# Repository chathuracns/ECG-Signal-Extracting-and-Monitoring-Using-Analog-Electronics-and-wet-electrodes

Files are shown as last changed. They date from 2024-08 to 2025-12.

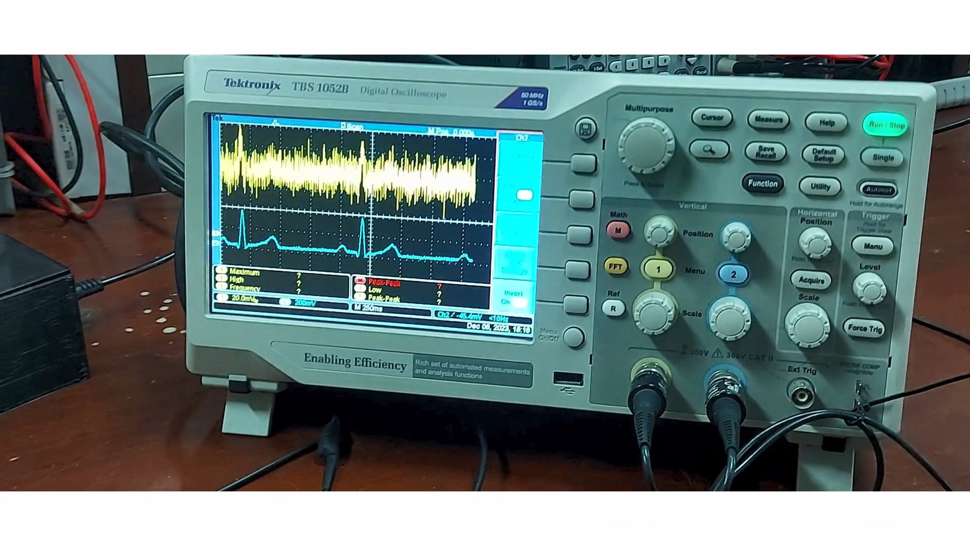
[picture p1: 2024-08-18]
media/amplified signal and denoised signal.png

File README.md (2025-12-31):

# Analog Heart Rate Monitor

## Overview
This project is an ECG (Electrocardiogram) waveform output and display heart monitor developed by a team of students from the Department of Electronic & Telecommunication Engineering, University of Moratuwa, Sri Lanka. The device is designed to amplify and display the small ECG voltage signal (0.1 mV to 10mV) while effectively managing noise interference.
[Video](https://www.linkedin.com/posts/chathura-weerasinghe-9a08bb213_ecg-biomedicalengineering-analogelectronics-activity-7230936167209189376-2sdM?utm_source=share&utm_medium=member_desktop)
## Features
- Right Leg Drive circuit for common-mode signal cancellation
- Instrumentation Amplifier for signal amplification and common noise elimination
- 1st order active Butterworth high pass filter
- 5th order active Bessel Thompson low pass filter
- Twin-T style notch filter for power line interference removal
- Analog components used throughout (except for the display unit)
- Adjustable gains and cutoff frequencies via variable resistors
- Custom-designed PCB and 3D-printed enclosure

## System Architecture
The system consists of the following main components:
1. Right Leg Drive Circuit
2. Instrumentation Amplifier
3. High Pass Filter
4. Low Pass Filter
5. Notch Filter
6. Power Supply Circuit
7. Display Circuit

## Key Components
- Operational Amplifier: TL072CP

## PCB Design
- Designed using Altium Designer
- Three separate PCBs: power circuit, heart monitor circuit, and display circuit
- Multi-layer design with ground pour and power routing

## Enclosure
- Designed using Solidworks
- Features removable top cover and detachable front for easy maintenance
- Includes power switch, tuning knob, and strategically placed connectorsi

## Contributors
- Kumarasinghe R.D (210321X)
- Rajapakshe N.N (210504L)
- Weerasinghe C.N (210687X)
- Withanawasam I.A (210732H)

## Acknowledgements
This project was submitted in partial fulfillment of the requirements for the module EN 2091 Laboratory Practice and Projects at the University of Moratuwa, Sri Lanka.

## License
GNU GENERAL PUBLIC LICENSE

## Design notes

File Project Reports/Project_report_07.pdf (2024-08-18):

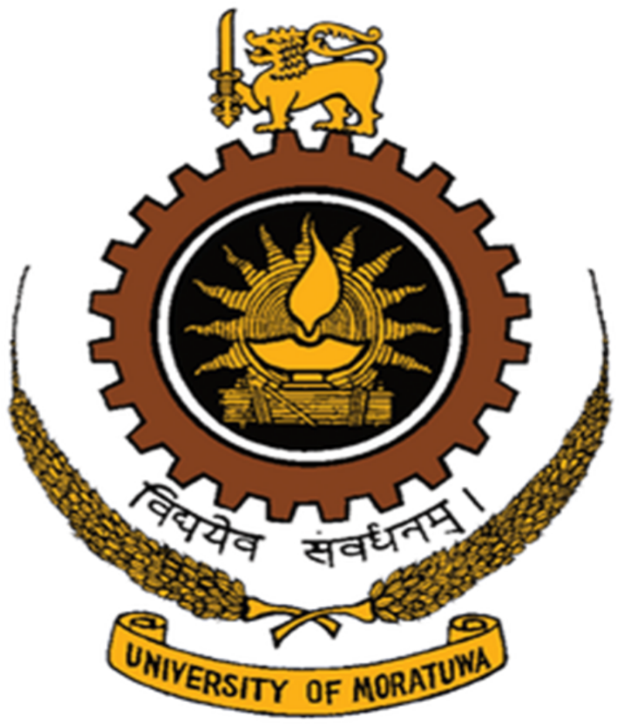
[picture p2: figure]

Department of Electronic & Telecommunication Engineering, University of Moratuwa, Sri Lanka.

# Analog Heart Rate Monitor

Group Members:

210321X | Kumarasinghe R.D
210504L | Rajapakshe N.N
210687X | Weerasinghe C.N
210732H | Withanawasam I.A

Submitted in partial fulfillment of the requirements for the module EN 2091 Laboratory Practice and Projects

6th December 2023

Analog Heart Rate Monitor | Group 07

## Contents

1 Introduction | 2
2 Functionality and Parameters | 2
2.1 Right Leg Drive | | | 2
2.2 Instrumentation Amplifier | | | 3
2.2.1 | Gain of the Instrumentation Amplifier | | 3
2.3 High Pass Filter | | 3
2.3.1 | Gain and Cutoff Frequency of High Pass Filter | | 3
2.4 Low Pass Filter | | 3
2.4.1 | Cutoff Frequency of Low Pass Filter | | 3
2.5 Notch Filter | | 3
2.5.1 | Cutoff Frequency of Notch Filter | | 4
3 System Architecture | 4
4 Component Selection | 4
5 PCB Design | 5
6 Enclosure Design | 5
7 Software Simulation and Hardware Testing | 5
8 Conclusion & Future Works | 5
9 Contribution of Group Members | 6
10 Bill of Materials | 6
11 References | 6
12 Appendix | 7

1

Abstract
Our project is an ECG waveform output and display heart monitor.The difficult task is to make the small range of the ECG voltage signal: 0.1 mV to 10mV, which is significantly impacted by noise.This is accomplished by a leg drive circuit, an a high pass filter, an instrumentation amplifier,both a notch filter and a low pass filter were utilized. 160 Hz was the bandwidth that was taken into consideration. Attaining this requires only analog electronic parts were employed. electronic digital elements were exclusively utilized in the digital circuit, breadboard, and simulation testing testing was carried out, along with PCB testing. the circuit’s functionality. An 3D enclosure was created and constructed to meet the requirements.

## 1 Introduction

An electrocardiogram (ECG) is a quick test that uses skin-attached sensors to measure electrical signals the heart produces with each beat in order to assess the heart’s rhythm and electrical activity. There is an increase in voltage between the right and left arms, with the right leg acting as a feedback mechanism. The ECG leads are used to obtain the voltages of the right arm, left arm, and right leg . The voltage signal’s frequency ranges from 0.01 Hz to 250 Hz, while its amplitude spans 0.1 mV to 10 mV.The small amplitude of the ECG raw signals and their susceptibility to noise and disturbances like electrostatic potentials, power line interference, RFI, electrode contact noise, stray capacitance, and bio signal artifacts introduced into an ECG by subject movement, respiration, and muscle tension make it difficult to amplify this signal. The ECG waves may occasionally be overpowered by noise, rendering the amplified signal meaningless.
We used only analog components when designing the ECG monitor, with the exception of the display unit, which amplifies and shows the voltage waveform mentioned above. We have described how we accomplished this in this report. The circuits listed below were used to generate the ECG waveform and provide the desired result.
1. Right Leg Drive Cicruit
2. Instrumentation Amplifier
3. 1st order active Butterworth high pass filter
4. 5th order active Bessel Thompson low pass filter
5. The Notch Filter

Moreover, the power supply and display screen were each connected to a different circuit, each with its own PCB. Variable resistors have been used in each filter circuit to modify the gains, reduce noise and disturbances based on the location, and compensate for unstable power supplies.

## 2 Functionality and Parameters

### 2.1 Right Leg Drive

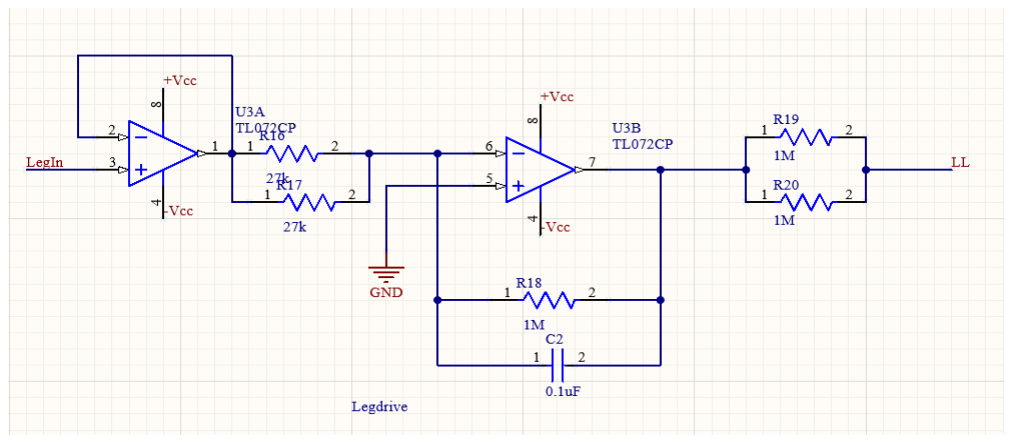
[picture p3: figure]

Figure 1: Right Leg Drive Circuit

By inverting, amplifying, and then feeding the signal back to the body through the right leg electrode, a right leg drive circuit is used to cancel the common-mode signal between the left and right arm electrodes.Additionally, the high value resistors in this circuit make sure that the patient is not exposed to a higher current.

2

### 2.2 Instrumentation Amplifier

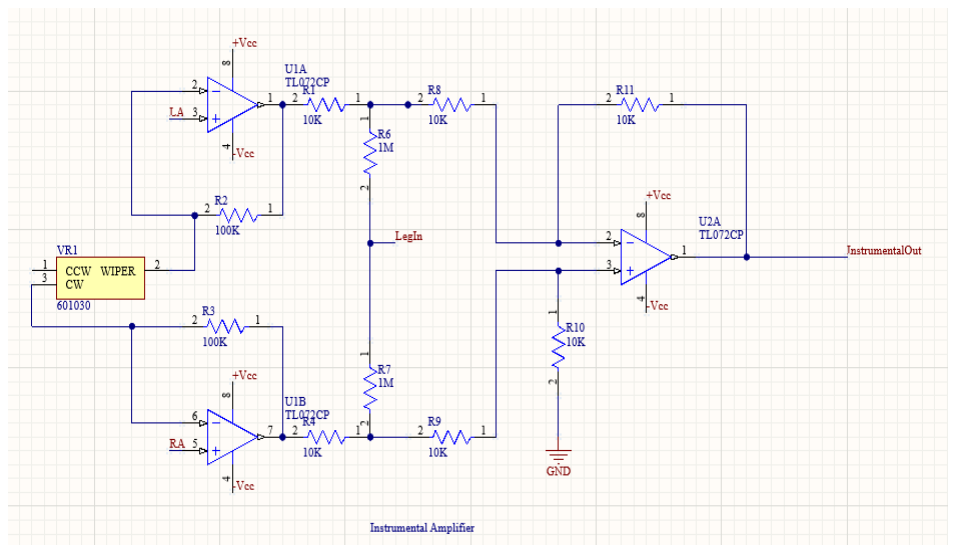
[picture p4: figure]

Figure 2:Instrumentation Amplifier

The signal is amplified using this circuit, which also eliminates common noise from the voltages coming from the ECG leads. This circuit converts the three inputs into a single output. Our circuit’s gain in the instrumentation amplifier is maintained between 20 and 50. We have adjusted the gain as needed by using a variable resistor.

### 2.2.1 Gain of the Instrumentation Ampli-

fier

Gain = R10
R9

(

R2 + R3 + V R1
V R1

)

Minimum Gain = 10kΩ
10kΩ(

2 × 100kΩ + 10kΩ
10kΩ | )
Minimum Gain = 21

### 2.3 High Pass Filter

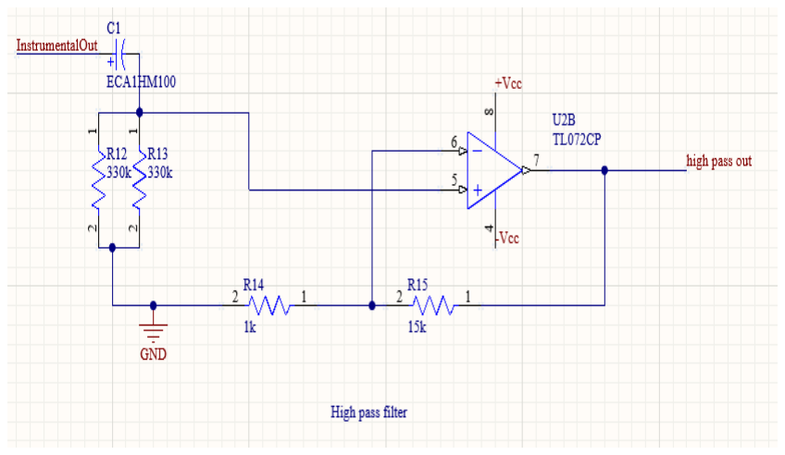
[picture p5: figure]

Figure 3:High Pass Filter

A first-order active inverting Butterworth filter has been used. In addition to amplifying the signal even more, this circuit removes the DC offset that developed between the electrodes. The gain of the filter is 16.

### 2.3.1 Gain and Cutoff Frequency of High

Pass Filter

Cutoff Frequency(Fc) = | 1 2π(R12//R13)C1
Cutoff Frequency = | 1 2π × 165kΩ × 10µF

Fc = 0.0965Hz

Gain =1 + R15

R14
Gain = 1 + 15kΩ
1kΩ = 16

### 2.4 Low Pass Filter

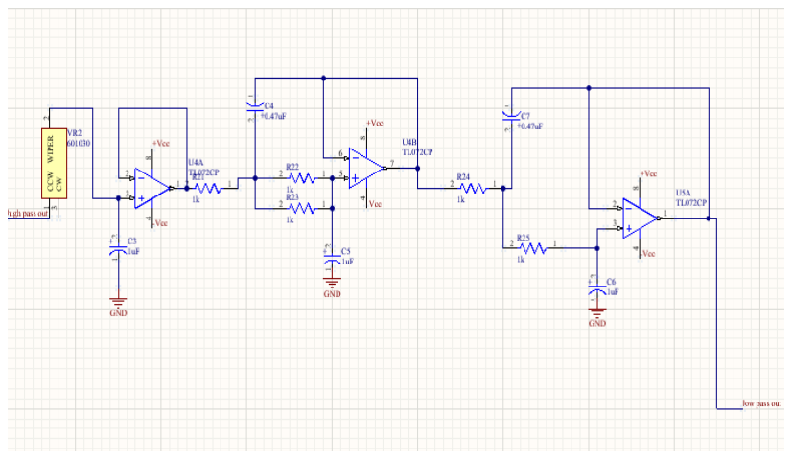
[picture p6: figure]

Figure 4:Low Pass Filter

Here, we employed a non-inverting Bessel Thompson filter of the fifth order. Two second order active filters and a series cascaded first order active filter make up this setup. Since each of their gains is a unity, the low pass filter’s total gain is also a unity. To change the cutoff frequency, we have employed a variable resistor.

### 2.4.1 Cutoff Frequency of Low Pass Filter

Cutoff Frequency = 1
2πV R2C3
Minimum Cutoff Frequency = | 1
2π × 10kΩ × 1µF
Minimum Cutoff Frequency = 15.91Hz

### 2.5 Notch Filter

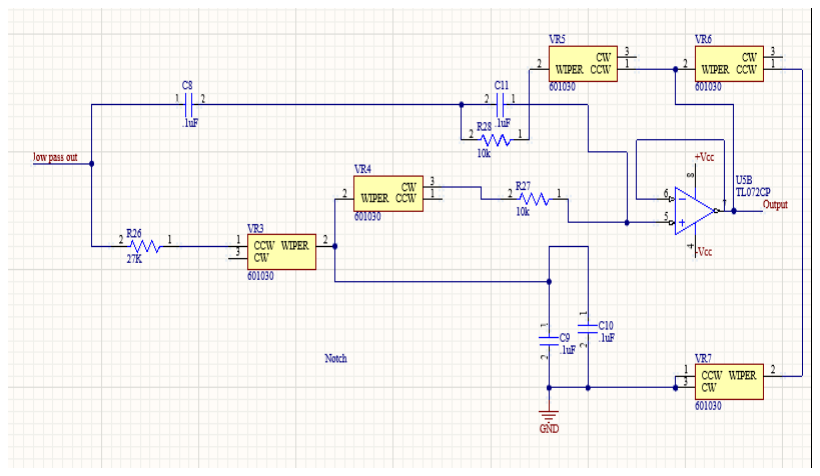
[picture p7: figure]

Figure 5:Notch Filter

3

In this case, a Twin-T style notch filter was utilized. This is how power line interference is removed. 50 Hz is the frequency of the notch filter as a result. To get the steeper roll-off, this calls for a high Q factor or a small transition bandwidth. One of the few RC networks that can provide an infinite deep notch at a specific frequency is the Twin-T notch filter. We have used a unity gain notch filter. Consequently, we applied this specific filter. The filter’s quality is determined by the Q factor, also referred to as the quality factor. This is adjusted as needed using a variable resistor. Three resistor values determine the notch frequency. Five tuners are used to adjust that as needed.

### 2.5.1 Cutoff Frequency of Notch Filter

Cutoff Frequency = | 1
2π(R26 + V R3)C8
Minimum Cutoff Frequency = | 1
2π × 37kΩ × 0.1µF
Minimum Cutoff Frequency = 43.015 Hz

## 3 System Architecture

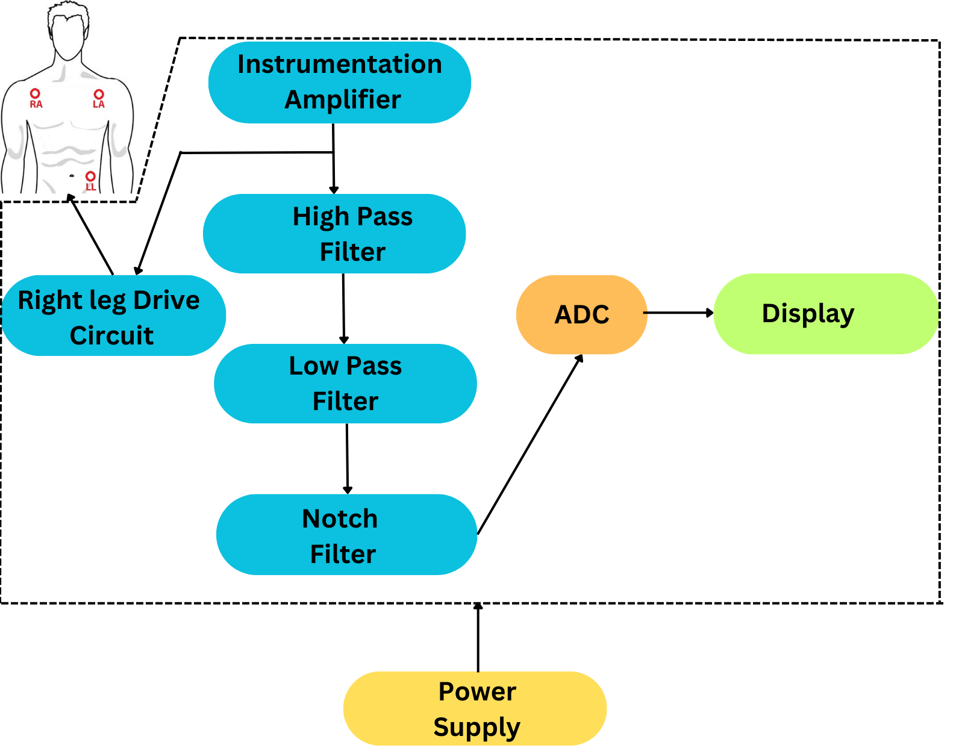
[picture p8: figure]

## 4 Component Selection

The selected operational amplifier for our analog ECG monitor is the TL072CP, chosen for its specific characteristics that align with the requirements of our design:
1.High Slew Rate (20 V/s typical): This feature enables quick responsiveness to rapid changes in input signals, making the TL072CP ideal for applications like ECG monitoring where signal fidelity is crucial.
2.Low Offset Voltage (1 mV typical): The TL072CP minimizes voltage differences between its input terminals when no signal is applied, ensuring accurate signal amplification.
3.Low Offset Voltage Drift (2 V/°C): With minimal drift over a wide temperature range, the amplifier’s performance remains stable.
4.Low Power Consumption (940 A/ch typical): The TL072CP is energy-efficient, drawing a modest current.

4

5.Wide Common-Mode and Differential Voltage Ranges:Common-mode input voltage range includes VCC+, allowing flexibility in signal levels. The differential voltage range accommodates various input signals. Low Input Bias and Offset Currents: These characteristics minimize the impact of input currents on the circuit.
6.Low Noise (18 nV/Hz typical at 1 kHz): Crucial for sensitive applications like ECG monitoring, the TL072CP maintains low noise levels.
7.Output Short-Circuit Protection: The amplifier is designed to withstand short-circuits at its output.
8.Low Total Harmonic Distortion (0.003% typical): Maintaining signal integrity, the TL072CP exhibits low distortion levels.
9.Wide Supply Voltage Range:Operates from ±2.25 V to ±20 V or 4.5 V to 40 V, providing flexibility in power supply options.

## 5 PCB Design

Altium Designer was used to design and print three printed circuit boards (PCBs): a power circuit, a heart monitor circuit, and a display circuit which are shown in figures 7,8 and 9. Three layers make up the ECG PCB. The ground pour and +15V top layer are poured into the bottom layer. For routing, both the top and bottom layers are utilized. To prevent capacitance from building up, the power supply PCB was printed in two layers, with the remaining layer being grounded, but routed in a single layer. Pours of ground are made into both lower layers. To facilitate easy replacement, all of the integrated circuits are coupled with IC bases. Pin headers and jumpers have been used to connect the ICs to external accessories.

## 6 Enclosure Design

The enclosure for our device was created using Solidworks, as shown in Figure 10. It’s designed for user convenience, featuring a removable top cover and detachable front, making it easy to fix or replace components. The front section has a power-on switch and a knob for tuning the instrumental amplifier, providing better operational control. For easy connectivity, the enclosure has strategically placed holes with adapters for the power cable and 3.5mm jack. This design focuses on user-friendly features. Additionally, a separate enclosure was designed specifically for the power supply circuit.

## 7 Software Simulation and Hardware Testing

Using LTSpice, we first simulated our complete circuit.After that, it’s put into practice on a breadboard with some modifications to get the least amount of noise in the signal. We can see the overall testing improvement from the oscilloscope display changes.

## 8 Conclusion & Future Works

Our future work involves integrating a display for immediate visual feedback on the ECG waveform, enhancing user understanding and experience. Real-time data plotting via serial communication has been implemented successfully, thanks to the easy integration of an ESP32 into our device. Even though the results of our early efforts were encouraging, we are dedicated to improving and streamlining the procedure to guarantee even higher graph plotting accuracy. Our goal is to remove any delays that may have occurred in the early phases, going above and beyond to provide a remarkable and accurate graphical depiction of the data.

5

## 9 Contribution of Group Members

Index Number | Contribution
1.210321X | Enclosure designing Circuit designing
2.210504L | Circuit designing Simulation
3.210687X | Circuit designing Enclosure designing
4.210732H | Pcb designing Simulation

## 10 Bill of Materials

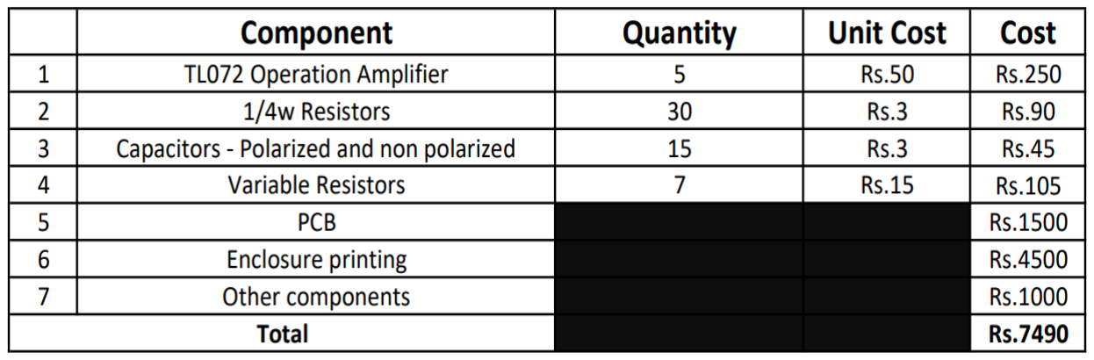
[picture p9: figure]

## 11 References

1. Du WY, Jose W. Design of an ECG sensor circuitry for cardiovascular disease diagnosis https://medcraveonline.com/IJBSBE/designof-an-ecg-sensor-circuitry-for-cardiovascular-disease-diagnosis.html 2.Article -https://electronics.stackexchange.com/questions/571823/choosingthe-right-op-amp-for-ecg-application

6

## 12 Appendix

Appendix 01- PCBs and Enclosure Design

PCB design using Altium Designer

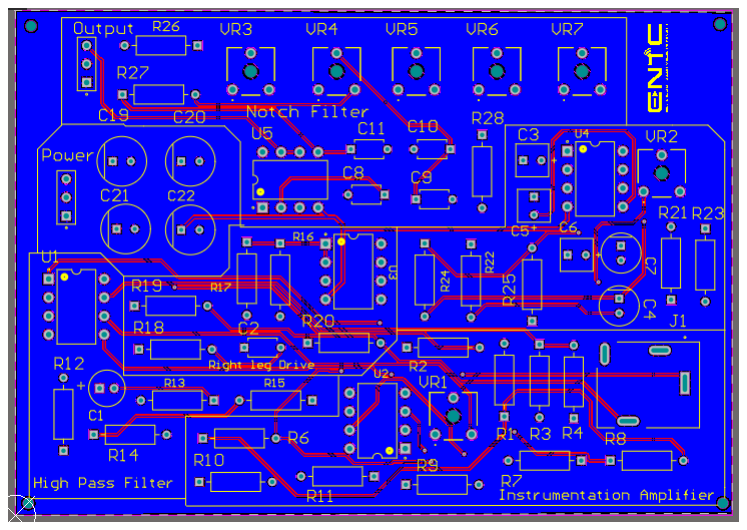
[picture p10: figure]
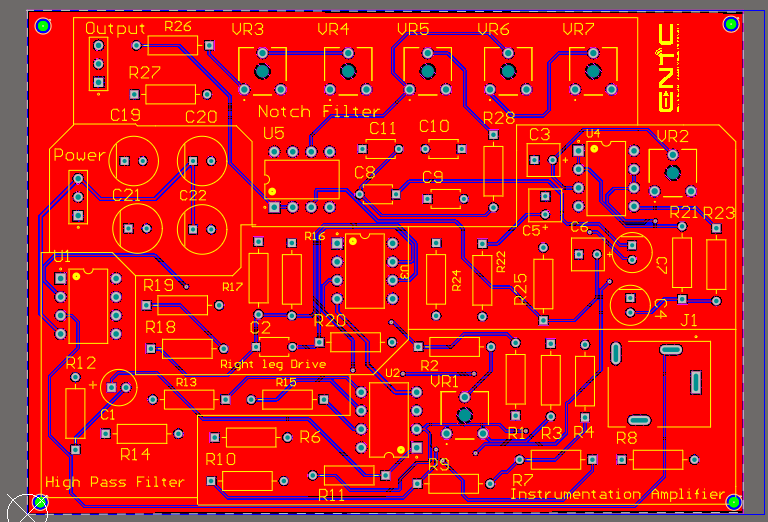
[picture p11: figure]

Figure 7:Top Layer | Figure 8:Bottom Layer

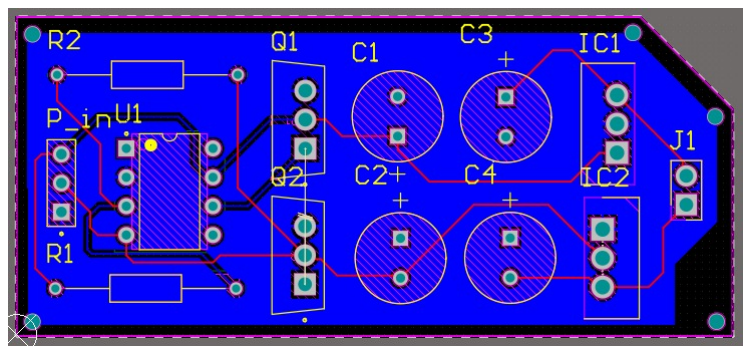
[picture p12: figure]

Figure 9:Power supply circuit

7

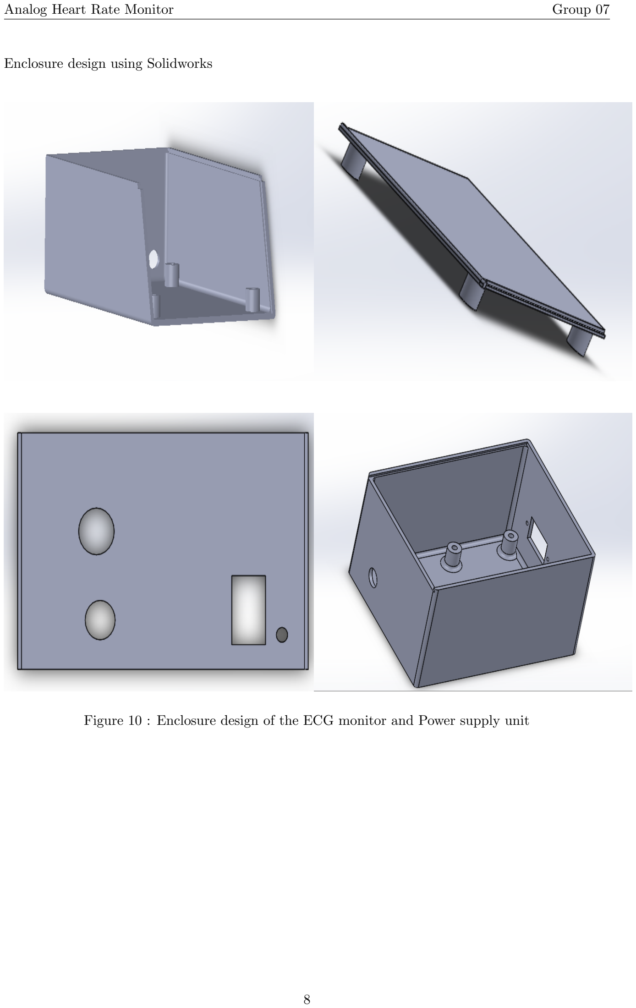
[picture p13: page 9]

Enclosure design using Solidworks

Figure 10 : Enclosure design of the ECG monitor and Power supply unit

8

Appendix 02- Simulation and Testing LT Spice Simulation and Results

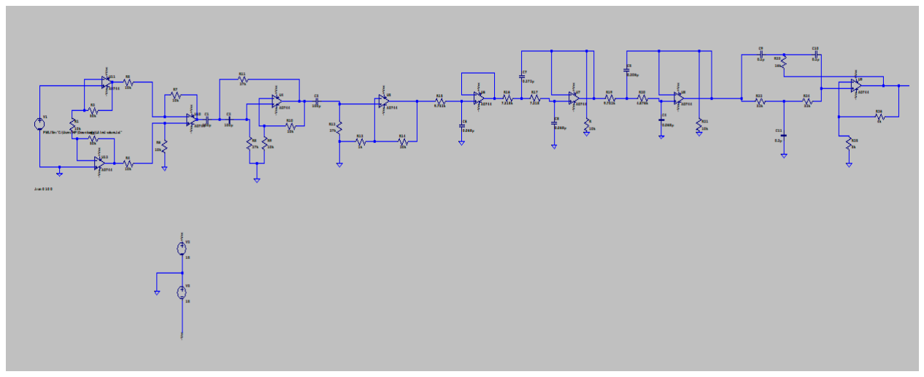
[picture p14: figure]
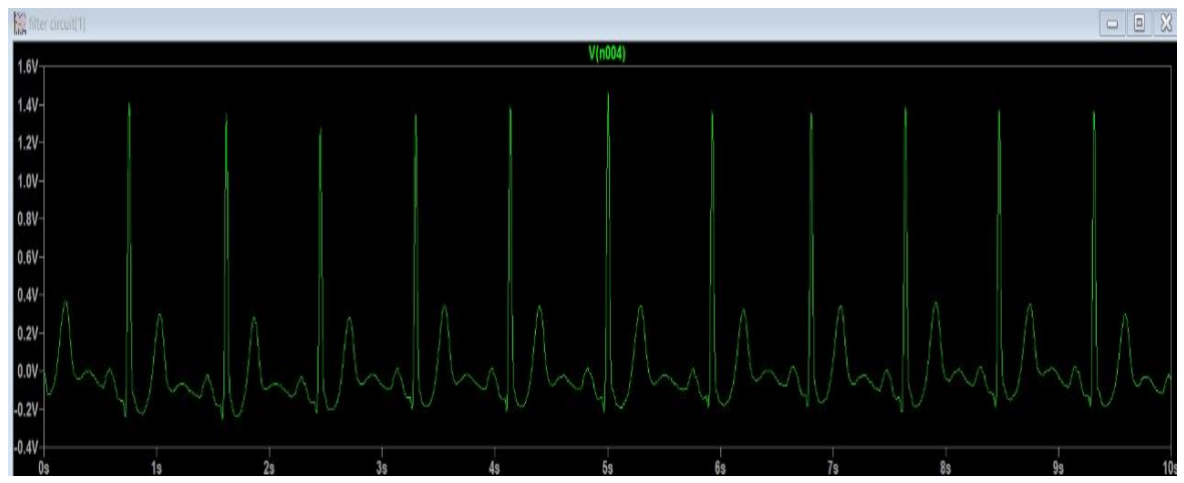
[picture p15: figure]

Figure 11 : LT spice simulation and resultant waveform

9

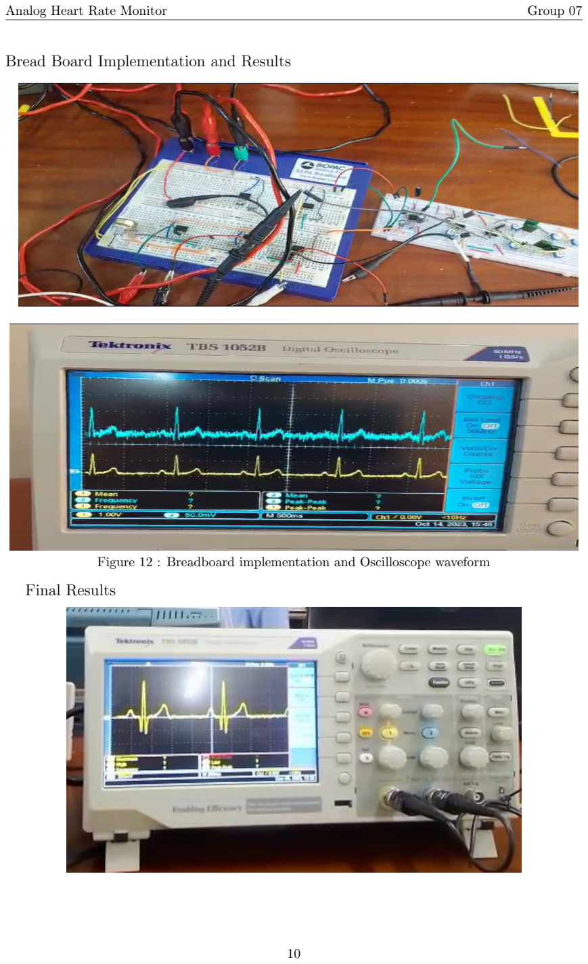
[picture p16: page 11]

Bread Board Implementation and Results

Figure 12 : Breadboard implementation and Oscilloscope waveform

Final Results

10

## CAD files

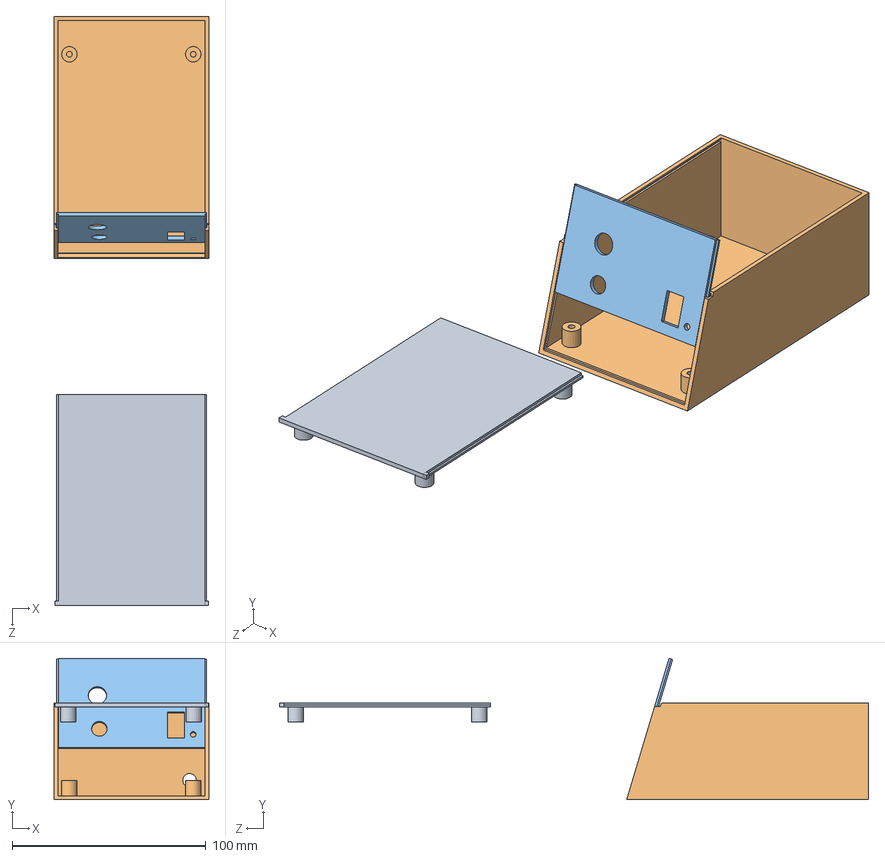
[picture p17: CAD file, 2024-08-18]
Enclosure Design/Main Enclosure/Assembly ECG.SLDASM
80.0 x 73.0 x 304.4 mm
Design 2 cover 2
Design 2
Design 2 cover 1

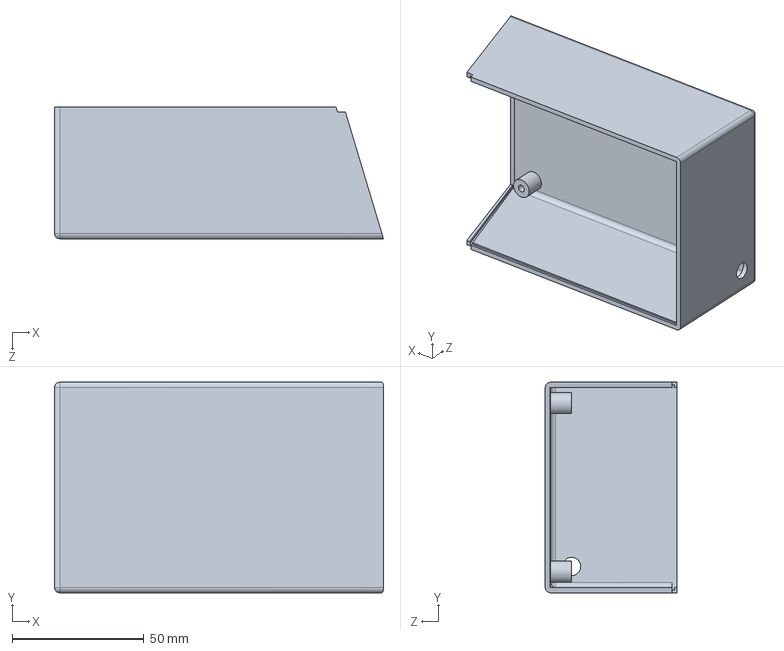
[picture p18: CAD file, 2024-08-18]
Enclosure Design/Main Enclosure/Enclosure ECG.SLDPRT
125.0 x 80.0 x 50.0 mm

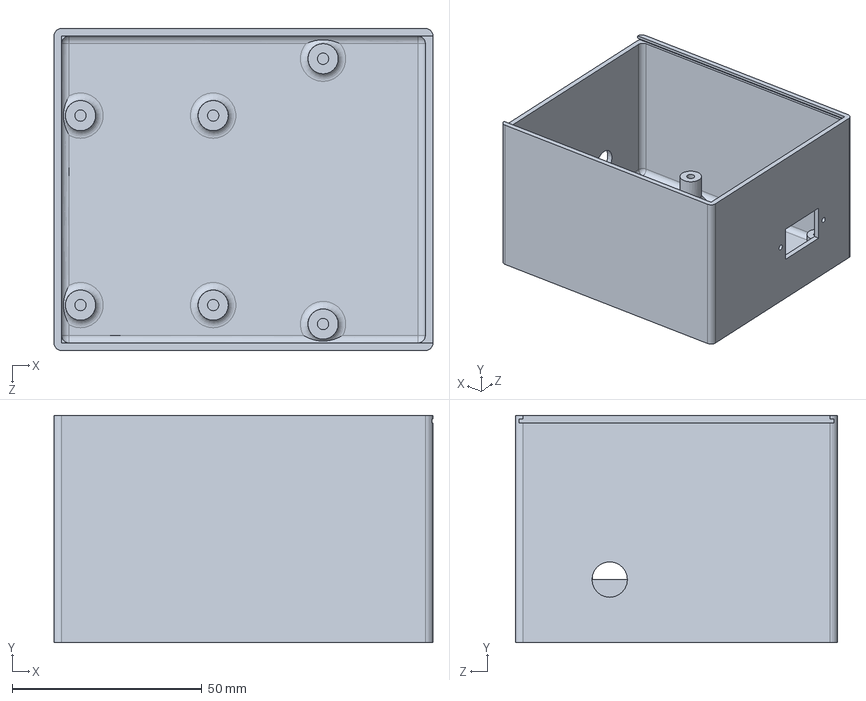
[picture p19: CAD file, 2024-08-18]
Enclosure Design/Power Unit Enclosre/Power supply enclosure.SLDPRT
100.0 x 60.0 x 85.0 mm

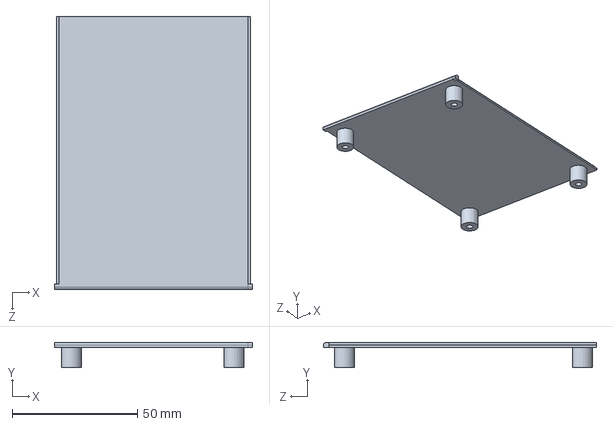
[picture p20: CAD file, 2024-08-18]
Enclosure Design/Main Enclosure/Cover 2.SLDPRT
79.2 x 10.0 x 109.0 mm

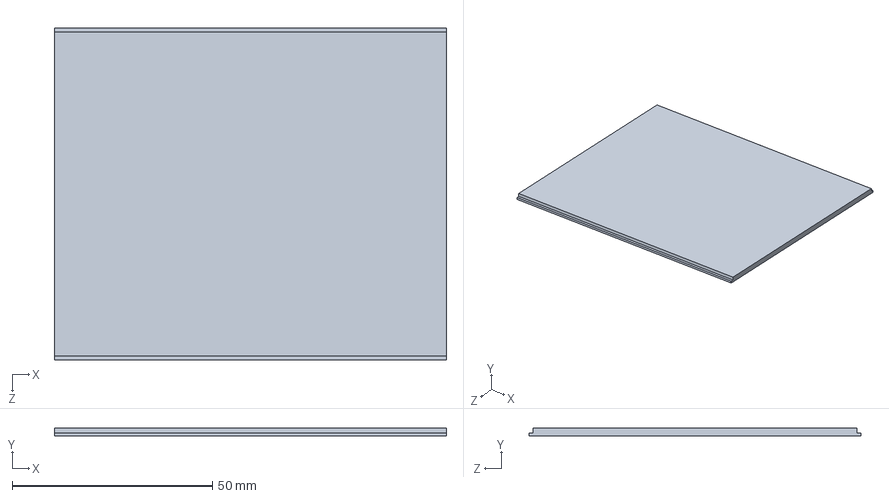
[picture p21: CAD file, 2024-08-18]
Enclosure Design/Power Unit Enclosre/Power supply cover.SLDPRT
98.0 x 2.00 x 83.0 mm

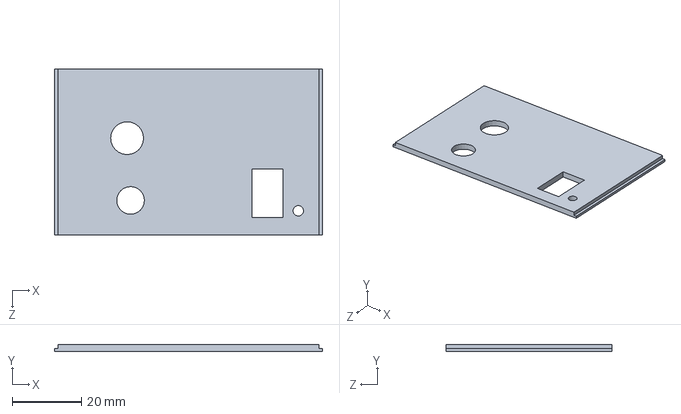
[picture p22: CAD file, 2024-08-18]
Enclosure Design/Main Enclosure/Cover 1.SLDPRT
77.5 x 2.00 x 48.0 mm
